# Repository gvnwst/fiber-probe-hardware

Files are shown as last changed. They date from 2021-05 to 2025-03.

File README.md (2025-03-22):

# Hardware designs for fiber probing

This is a collection of designs I started creating during my graduate career at MIT. 
I was frustrated by the poor selection of both commercial and custom options for the mounting fiber optics in a manner suitable for probing photonic integrated circuits -- particularly in the case of vertical grating couplers. 
In the history of my lab (at the least, what fraction I am aware of) there were at least four different custom approaches.
The motivations for each varied: simplicity/ease of machining, variability in fiber angle, ability to hold fiber in an intermediate clamp, and so on.

Anyway, these are my version(s). 

## Project structure
In its first iteration, there are just one or two variations of fiber holders, and one type of die mounting chuck. 
Most of my designs are made in solidworks 2018 (as time has gone on, a lot of these are Solidworks 2024), so you'll need to be able to open or convert these files to another format if you want to modify anything. 
Other filetypes (`.stl`, etc) may be made available if there is interest.

Each version of a design should be housed in its own directory and include: 
1. 3D models of all required custom parts, suitable for being sent to rapid prototyping services (`plethora`, `xometry`, and `protolabs` to name three I've used)
    1. If the new design is an update of only _part_ of a previous design, the un-changed 3D models should not be replicated. However, there should exist clear references in...
3. A bill of materials, including non-custom parts (fittings, needles, etc)
4. A document with a brief description of the design and its intended use case. This may be in the same file as the BOM. 
5. A subdirectory, often called `auxiliary files`, that stores *extra* CAD files which may be useful (e.g.  assemblies, `.stl` files for prototyping on a 3D printer). These are not designs that need to be sent out for manufacture.

## A note on license and derivative works
A creative commons license was chosen for this repository, and you the reader are encouraged to use and upgrade these designs! 
I would additionally ask that if you think up a genius improvement, or are inspired to create something better, that you also share those designs publically. 
You can do that here, by making a pull request, or through your own project -- I'm happy to reference other projects in this documentation. 
Anything to avoid some other poor grad student from going through the process, again.

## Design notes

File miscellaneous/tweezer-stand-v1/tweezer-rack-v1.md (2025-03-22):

# Tweezer Rack Version 1

This design is a rack which holds tweezers, particularly the types and sizes used to manipulate small chips up to 150 mm wafers. 
It is intended to be rigidly affixed to a table or surface via the pair of holes on the bottom flange (or adhesive tape, if no appropriate surface for threading into/drilling through is available). 
Flush-head studs are screwed into the threaded holes from the back side of the main flange. 
Tweezers are hung off this, akin to a coat rack. 
Alternately, tweezers may be inserted into the top rectangular slots, handle-first. 
The round holes on each side hold many standard size pens or sharpies.

It is stable with tweezers hung on the primary surface, but may be tippy if only the top slots are loaded.

The design is a replica of the tweezer stands used in MIT's cleanroom facilities (MIT Nano), the designs for which were kindly provided by Jorg Scholvin.
Jorg had these manufactured at [send-cut-send](https://sendcutsend.com/). They provide anodized finishes and can mount flush studs (0.5 inch) into the threaded holes.

A ready-to-manufacture `DXF` of the flattened part is included in the design directory. 

## Bill of Materials

| Description  | Vendor/Manufacturer | Part Number | Quantity | Comments |
| ------------- | ------------- | ------------- | ------------- | ---- |
| Tweezer Rack 	|	Custom	|	tweezer-rack-v1	| 	1	| 	 	|

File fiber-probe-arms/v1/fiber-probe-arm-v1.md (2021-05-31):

# fiber probe arm v1: Angle-adjustable mounting with rigid needle guides

This design is an arm for holding fiber optics with an adjustable angle (15 deg. nominal), with flexibility for using PM fiber (some in-place rotational adjustability).

The fiber itself is held in steel Luer-lock needles whose inside diameter is slightly larger than that of a fiber with its polymer coating intact.
These needles are clamped into a block which has a guide slot machined into it, and the block is mounted on a flange which pivots around a screw.
Another screw provides a few degrees of adjustability in the fiber angle, with small springs providing the counter-action to the adjustment screw.
With the pivot point at the end of the arm, this is much more convenient than using a goniometer to mount a fixed arm, but it's still not gimbaled around the fiber tip.

### Comments on assembly
The fiber may be affixed in the needles a few ways. Most obvious is simply potting with epoxy/glue, for cleaved-facet fibers (which frequently contact the die) the inability to re-cleave can be a problem.
Alternatively, I have been using the last item in the BOM to sort of strain-relieve the fiber into the Luer-lock end of the needle.
I cut a ~1 cm long section of the rubber rod and use a razor blade to make a slice along its length, slightly deeper than the center of the rod.
This should look a bit like a hot dog bun -- and the fiber rests inside the piece much like a hot dog in its bun!
The high friction coefficient of the rubber provides a good hold on the fiber, and the rubber can be jammed into the Luer needle's end.

You may find it helpful to buy a slightly over-sized rubber rod and taper the end which will be stuck into the needle.
I create a "taper" by just making a single angled cut from ~the center of the needle end to the outside of the rod about 50% of the way along its length.
See the file `rubber_stopper_example.SLDPRT` for a (non-scaled) representation of this.

To get the balance of screw tightness and spring restoring force right, I actually use two springs -- one mounted into each dowel pin slot.
You could just find stronger springs.

## Bill of Materials

| Description  | Vendor/Manufacturer | Part Number | Quantity | Comments |
| ------------- | ------------- | ------------- | ------------- | ---- |
| Arm cantilever 	|	Custom	|	 fiber-arm-cantilever-v1		| 	1	| 	 	|
| Mounting block	|	Custom 	| 	fiber-mount-block-v1	|	1	|	 |
| Block flange 	|	Custom 	| 	fiber-flange-v1	|	1	|	Should be sheet metal fabbed from stainless steel sheet |
| Clamping plate	|	Custom 	| 	fiber-clamp-plate-v1	|	1	|	 |
| Dowel pins | McMaster | 	97395A403	|	1	| Can use 2	|
| Springs 	 | McMaster | 9432K210		|	1	|  Can use 2	|
| 2-56 screws, 1/8" 	 | McMaster | 	92196A074	|	4	| Mount block to flange, clamp plate to block  |
| 2-56 screws, 1/4" 	 | McMaster | 	92196A077	|	1	| Mount flange to arm cantilever |
| 2-56 screws, 1/2" 	 | McMaster | 	92196A081	|	1	| Adjustment screw for tilt  |
| 2-56 lock washers 	 | McMaster | 92147A410		|	1	|  |
| Luer-lock needles 	 | McMaster | 6710A31		|	1	| 23 gauge |
| Rubber rod 	 | McMaster | 		|	1	| Diameter?? |

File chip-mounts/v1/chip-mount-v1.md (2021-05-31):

# chip mount v1: a low-upward-expansion TEC vacuum chuck for small to medium die

This design is a vacuum chip mount with thermal control through a TEC.
It is designed to minimize thermal expansion-induced vertical displacement in chip position -- critical for stable fiber-die position during thermal sweeps.
The expansion is minimized in two ways: the chuck on which the die sits is supported by a top-mounted flange, such that the expansion happens _downward_, and the flange itself is made from low-thermal-expansion steel.
In order to support vacuum lines/the bulky NPT-threaded hose nipple, the chuck is somewhat thick.
For this reason, I have them machined from high thermal conductivity copper.
Wiring from the thermistor and TEC to your TEC driver are left up to you.

The provided flange design is set up to mount to a Newport Ultralign 561D-YZ stage, but it mounts to anything with 1" separated #8 screws.

A glaring omission from the BOM below is a heatsink to mount on the TEC's hot side.
I haven't been able to find a good quality copper/aluminum heatsink in the correct form factor -- for my probe stations, I'm using a large skived copper heatsink (scrounged from the lab) which I cut to the correct size using a bandsaw (the rough edges can be cleaned up with a dremel).

Another heatsink option would be water cooling, if your lab has extra chillers around.
A block for liquid cooling the TEC would be pretty easy to design.
I have avoided it so far due to concerns about vibration of the heatsink, but I have never quantitatively tested these concerns.

## Bill of Materials

| Description  | Vendor/Manufacturer | Part Number | Quantity | Comments |
| ------------- | ------------- | ------------- | ------------- | ---- |
| Chip mount 	|	Custom	|	 mount-chuck-v1		| 	1	| 	Copper 	|
| Mounting flange	|	Custom 	| 	mount-flange-v1	|	1	|	Stainless steel |
| Vacuum hose fitting | McMaster | 5463K54		|	1	|	|
| Vacuum hose 	 | McMaster | 5233K52		|	1	| 	|
| Brass screws 	 | McMaster | 5233K52		|	1	| Attach chuck to flange |
| TEC module 	|	Digikey	|	1681-1190-ND |	1	|	|
| Thermistor (10k) |	Digikey |	235-1423-ND | 1 |	|

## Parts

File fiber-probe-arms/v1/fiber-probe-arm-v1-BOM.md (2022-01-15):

# fiber probe arm v1: Angle-adjustable mounting with rigid needle guides

This design is an arm for holding fiber optics with an adjustable angle (15 deg. nominal), with flexibility for using PM fiber (some in-place rotational adjustability).

The fiber itself is held in steel Luer-lock needles whose inside diameter is slightly larger than that of a fiber with its polymer coating intact.
These needles are clamped into a block which has a guide slot machined into it, and the block is mounted on a flange which pivots around a screw.
Another screw provides a few degrees of adjustability in the fiber angle, with small springs providing the counter-action to the adjustment screw.
With the pivot point at the end of the arm, this is much more convenient than using a goniometer to mount a fixed arm, but it's still not gimbaled around the fiber tip.

### Comments on assembly
The fiber may be affixed in the needles a few ways. Most obvious is simply potting with epoxy/glue, for cleaved-facet fibers (which frequently contact the die) the inability to re-cleave can be a problem.
Alternatively, I have used some soft rubber rod to sort of strain-relieve the fiber into the Luer-lock end of the needle.
I cut a ~1 cm long section of the rubber rod and use a razor blade to make a slice along its length, slightly deeper than the center of the rod.
This should look a bit like a hot dog bun -- and the fiber rests inside the piece much like a hot dog in its bun!
The high friction coefficient of the rubber provides a good hold on the fiber, and the rubber can be jammed into the Luer needle's end.

You may find it helpful to buy a slightly over-sized rubber rod and taper the end which will be stuck into the needle.
I create a "taper" by just making a single angled cut from ~the center of the needle end to the outside of the rod about 50% of the way along its length.
See the file `rubber_stopper_example.SLDPRT` for a (non-scaled) representation of this.

Alternatively (and what I actually do now, it's so much better) I designed some fixtures which clamp onto the end of the Luer-lock needles and magnetically hold the fiber in place (analogous to products from Thorlabs, Luminos, etc). 

To get the balance of angle adjustment screw screw tightness and spring restoring force right, I actually use two springs -- one mounted into each dowel pin slot.
You could just find stronger springs.

## Bill of Materials

| Description  | Vendor/Manufacturer | Part Number | Quantity | Comments |
| ------------- | ------------- | ------------- | ------------- | ---- |
| Arm cantilever 	|	Custom	|	 fiber-arm-cantilever-v1		| 	1	| 	 	|
| Mounting block	|	Custom 	| 	fiber-mount-block-v1	|	1	|	 |
| Block flange 	|	Custom 	| 	fiber-flange-v1	|	1	|	Should be sheet metal fabbed from stainless steel sheet |
| Clamping plate	|	Custom 	| 	fiber-clamp-plate-v1	|	1	|	 |
| Dowel pins | McMaster | 	97395A403	|	1	| Can use 2	|
| Springs 	 | McMaster | 9432K210		|	1	|  Can use 2	|
| 2-56 screws, 1/8" 	 | McMaster | 	92196A074	|	4	| Mount block to flange, clamp plate to block  |
| 2-56 screws, 1/4" 	 | McMaster | 	92196A077	|	1	| Mount flange to arm cantilever |
| 2-56 screws, 1/2" 	 | McMaster | 	92196A081	|	1	| Adjustment screw for tilt  |
| 2-56 lock washers 	 | McMaster | 92147A410		|	1	|  |
| Luer-lock needles 	 | McMaster | 6710A31		|	1	| 23 gauge |

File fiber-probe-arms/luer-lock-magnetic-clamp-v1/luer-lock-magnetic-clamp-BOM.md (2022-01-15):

# Magnetic clamping fiber holders for Luer-Lock needles

A weakness of the Luer-Lock needles is that the fibers are difficult to hold.
A trimmed rubber grommet works, but it's difficult. Inspired by the magnetic fiber clamps on our fusion splicer (and cleaver, etc, magnetic portion similar to [these](https://www.ozoptics.com/news/pr_173.html)), here's a piece of hardware which clamps onto the steel Luer lock needles and magnetically clamps your fibers into place. Easy-peasy fiber length adjustment.
It should also allow rotational adjustment for PM fiber, just loosen one of the collar screws and turn the whole chuck. More permanent clamping of the fiber may require adjustments.

The rubber sheet will need to be cut into a strip about 0.2" wide and just under 0.5" wide, then glued into the appropriately-sized slot on the clamp flange.
This will provide a friction surface to hold the fiber into the groove.

BOM is *per fiber clamp*. You'll want two (at least) for each probe station, input and output fibers.
Of course, some items have a large quantity and do not need multiples ordered when constructing more than one fiber clamp.

The base and collar are designed for ~perfect fitting around the Luer-Lock needle necks.
You may find that it's a bit loose. To solve this, simply take the collar and rub it (the face which contacts the base) against some medium-grit sandpaper until a few thousandths are taken off, so
Re-check fit, keep going if necessary -- you can take off a lot, needbe.

## Bill of Materials

| Description  | Vendor/Manufacturer | Part Number | Quantity | Comments |
| ------------- | ------------- | ------------- | ------------- | ---- |
| Base    |	Custom	|	 	clamp-base-v1	| 	1	| 	Aluminum 	|
| Flange  |	Custom 	|  clamp-flange-v1 |	1	|	Aluminum or steel  |
| Collar  |	Custom 	|  clamp-collar-v1 |	1	|	Aluminum |
| Dowel rod | McMaster | 98381A423	|	1 | Pack of 50	|
| Rare earth magnets | McMaster | 5862K101	|	3 | 	|
| Contact adjustment screw | McMaster | 92765A005	|	1 | 4-40 x 3/16" setscrew, alloy steel	|
| Rubber rod | McMaster | 1775T21	|	1 |  Foot, 40A durometer (medium soft)	|

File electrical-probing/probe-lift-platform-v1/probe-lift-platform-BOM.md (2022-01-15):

# lever-lifted electrical probe mount v1: A small, cheap version of the platform lifting you get on real probe stations

## Bill of Materials

| Description  | Vendor/Manufacturer | Part Number | Quantity | Comments |
| ------------- | ------------- | ------------- | ------------- | ---- |
| Cam 	         |	Custom	|	 cam-v1		| 	2	| 	Steel recommended 	|
| Front spindle  |	Custom 	|  spindle-v1 |	1	|	 |
| Rear spindle	 |	Custom 	|  rear_spindle-v1 |	2	|	Frontward for chassis rigidity |
| Chassis leg	   |	Custom 	|  chassis_side-v1 |	1	|	 |
| Top surface	   |	Custom 	|  top_plate-v1    |	1	|	Steel or other magnetic |
| Top surface	   |	Custom 	|  top_plate-v1    |	1	|	Steel or other magnetic |
| PTFE spindle bearing for front  | McMaster | 2706T17		|	2 |	|
| PTFE spindle bearing for rear   | McMaster | 2706T13		|	2 |	|
| Bearing housing for rear        | McMaster | 3971N17    |	2 |	|
| Dowel pins | McMaster | 	97395A403	|	1	| Shared with fiber probe arms v1	|
| 10-32 hex nut | McMaster | 	91841A195	|	1	| Box of 100. Lock height adjustment	|
| 10-32 carriage bolt | McMaster | 	92356A257	|	1	| Box of 50. Set height adjustment	|
| #4-40 bolts | McMaster | 	92196A109	|	1	| Attach lever arm to cam. 7/16". 3/8" or 1/2" should also work |
| #4-40 lock washer | McMaster | 	92147A415	|	1	| Attach lever arm to cam. |
| Lever arm grip | McMaster | 	9282K83	|	1	| Set of six	|
| Lever arm rest | McMaster | 	92196A546	|	1	| Box of 25. Partially-threaded machine screw. Also need nut. 	|
| Lever arm rest adjustment | McMaster | 	94355A700	|	1	| 4-40 setscrew. Also need nut. |

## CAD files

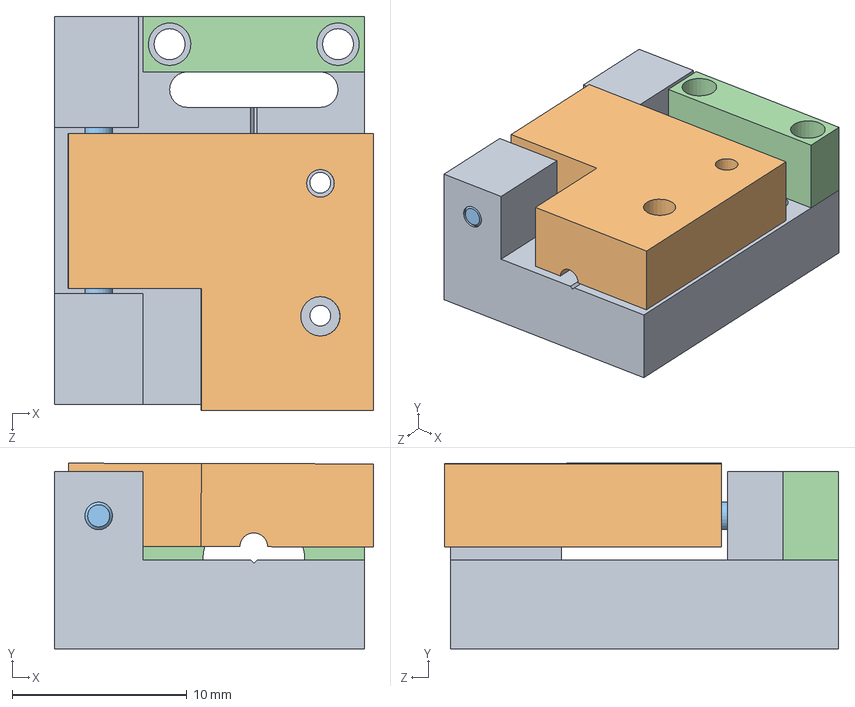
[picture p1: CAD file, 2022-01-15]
fiber-probe-arms/luer-lock-magnetic-clamp-v1/auxiliary files/Magnetic fiber clamp assembly v1.SLDASM
18.3 x 10.6 x 22.6 mm
clamp-base-v1
clamp-flange-v1
98381A423_ALLOY STEEL DOWEL PIN
clamp-collar-v1

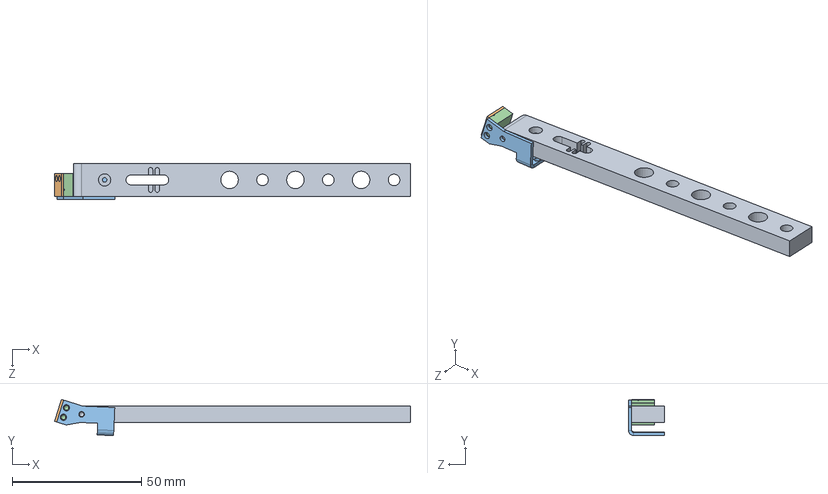
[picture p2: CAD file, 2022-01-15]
fiber-probe-arms/v1/fiber-assembly-v1.SLDASM
137.5 x 14.0 x 13.9 mm
fiber-arm-cantilever-v1
fiber-clamp-plate-v1
fiber-flange-v1
fiber-mount-block-v1

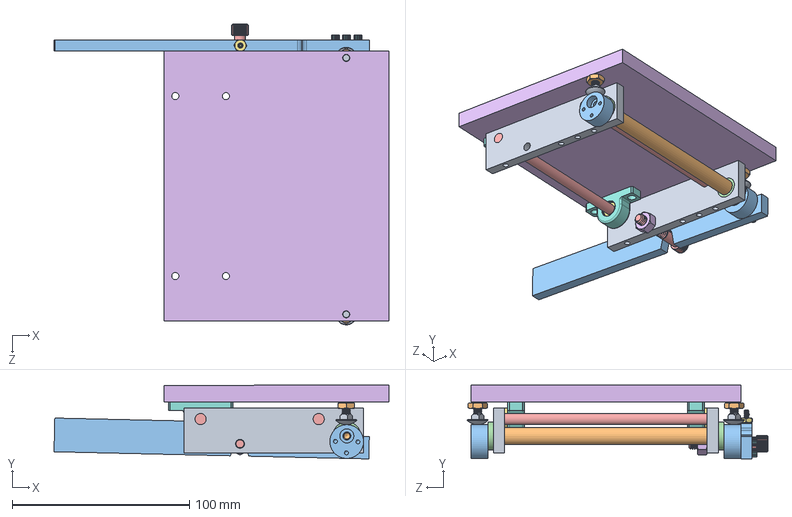
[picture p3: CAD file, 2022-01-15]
electrical-probing/probe-lift-platform-v1/auxiliary-cad/probe-lift-platform-assembly.SLDASM
189.1 x 41.7 x 169.8 mm
chassis_side-v1 x 2
front_spindle-v1
cam-v1 x 2
ptfe-spindle x 2
rear_spindle-v1 x 2
top_plate-v1
ptfe-spindle-rear x 2
bearing-housing x 2
10-32-0625_carriage_bolt x 2
10-32 hex nut x 2
lever-arm-v1
4-40 setscrew
14-20 bolt
14-20 nut
4-40 nut
4-40 7-16in screw x 3

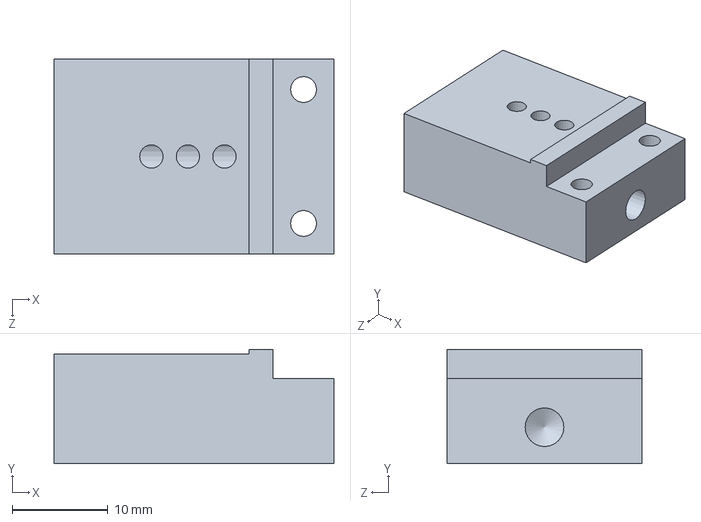
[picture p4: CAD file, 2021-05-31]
chip-mounts/v1/mount-chuck-v1.SLDPRT
29.2 x 11.9 x 20.3 mm

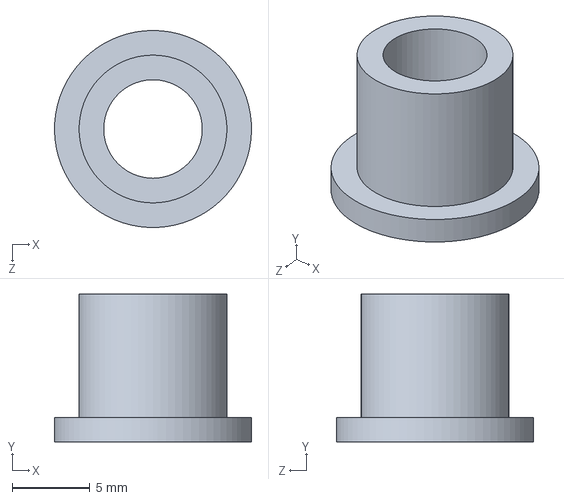
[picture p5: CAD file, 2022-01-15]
electrical-probing/probe-lift-platform-v1/auxiliary-cad/ptfe-spindle-rear.SLDPRT
12.7 x 9.53 x 12.7 mm

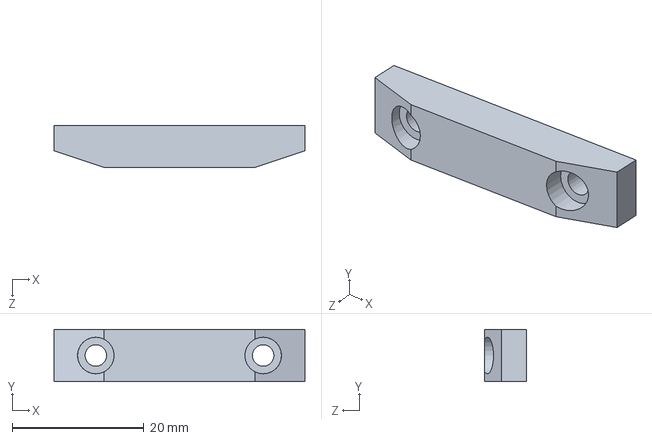
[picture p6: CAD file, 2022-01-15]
electrical-probing/probe-lift-platform-v1/cam_runner-v1.SLDPRT
38.1 x 7.94 x 6.35 mm

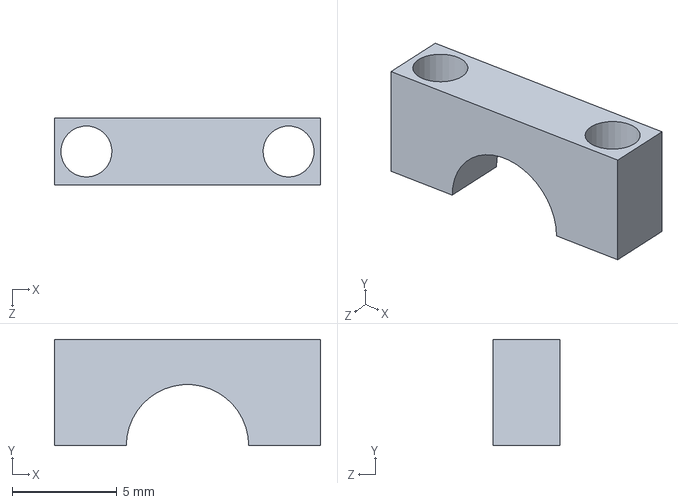
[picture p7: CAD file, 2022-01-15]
fiber-probe-arms/luer-lock-magnetic-clamp-v1/clamp-collar-v1.SLDPRT
12.7 x 5.08 x 3.17 mm

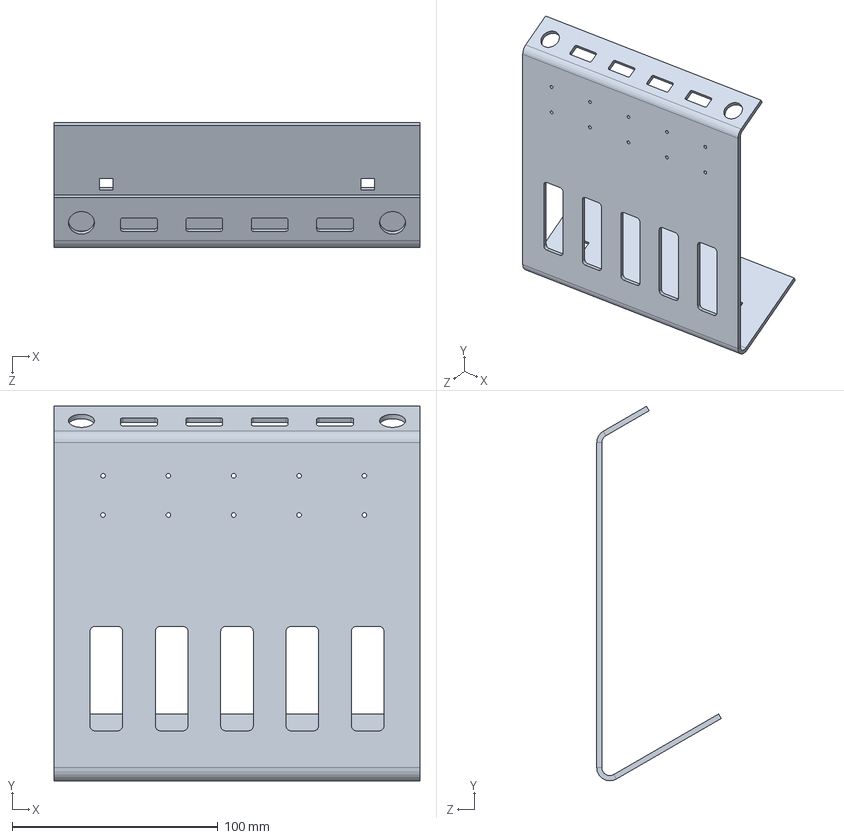
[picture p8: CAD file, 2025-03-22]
miscellaneous/tweezer-stand-v1/tweezer-rack-v1.SLDPRT
177.8 x 182.0 x 60.5 mm

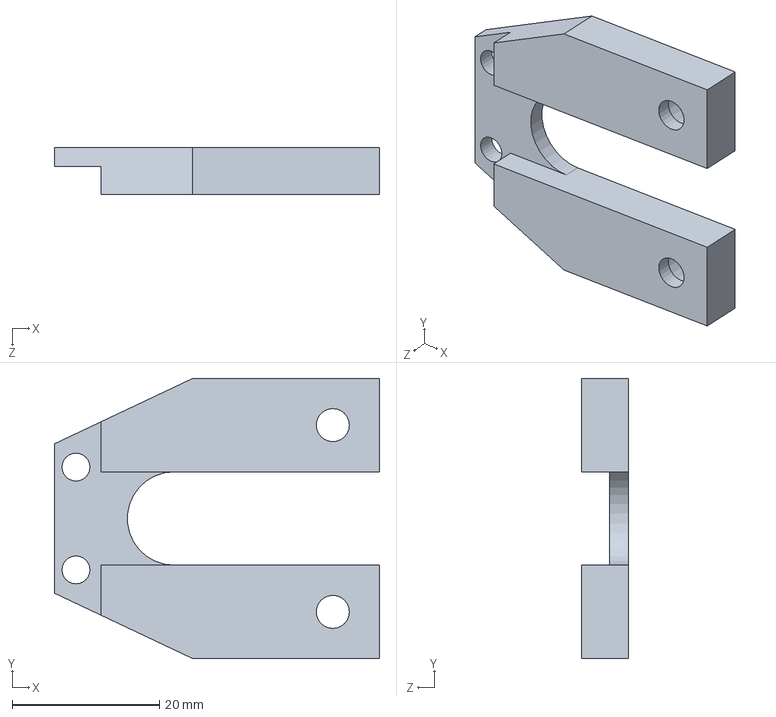
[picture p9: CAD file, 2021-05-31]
chip-mounts/v1/mount-flange-v1.SLDPRT
44.2 x 38.1 x 6.35 mm

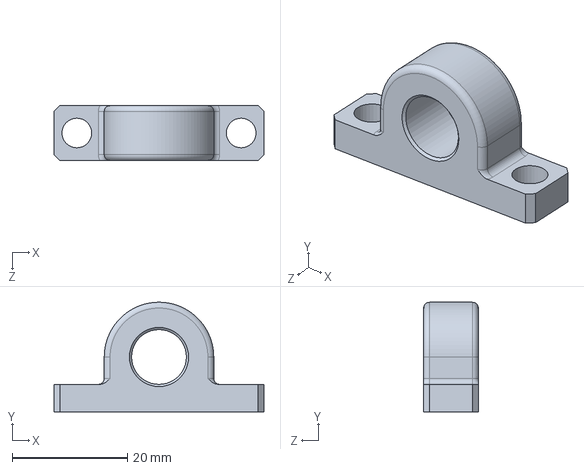
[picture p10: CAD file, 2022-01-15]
electrical-probing/probe-lift-platform-v1/auxiliary-cad/bearing-housing.SLDPRT
36.5 x 19.0 x 9.53 mm

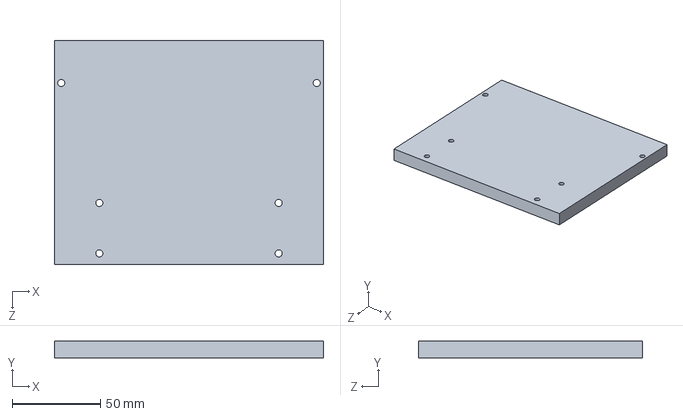
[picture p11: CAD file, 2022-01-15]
electrical-probing/probe-lift-platform-v1/top_plate-v1.SLDPRT
152.4 x 9.53 x 127.0 mm

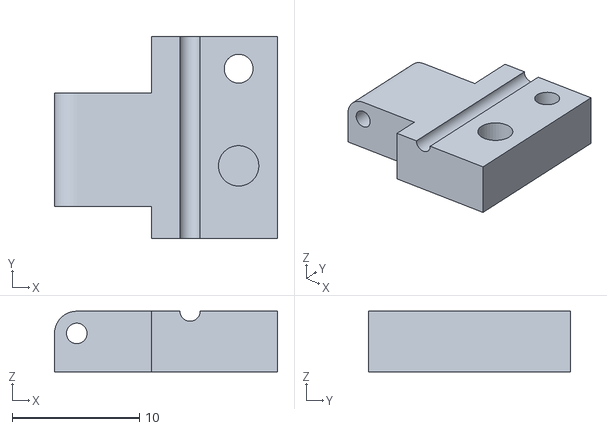
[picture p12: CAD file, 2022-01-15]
fiber-probe-arms/luer-lock-magnetic-clamp-v1/auxiliary files/clamp-flange-v1.STL
17.5 x 15.9 x 4.76

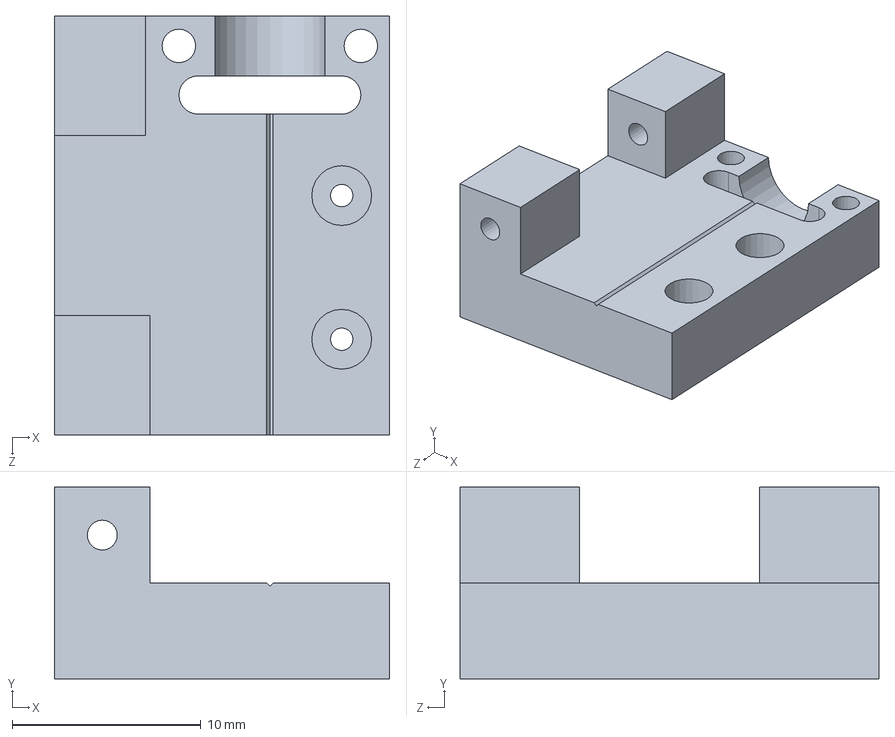
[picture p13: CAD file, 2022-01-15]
fiber-probe-arms/luer-lock-magnetic-clamp-v1/clamp-base-v1.SLDPRT
17.8 x 10.2 x 22.2 mm

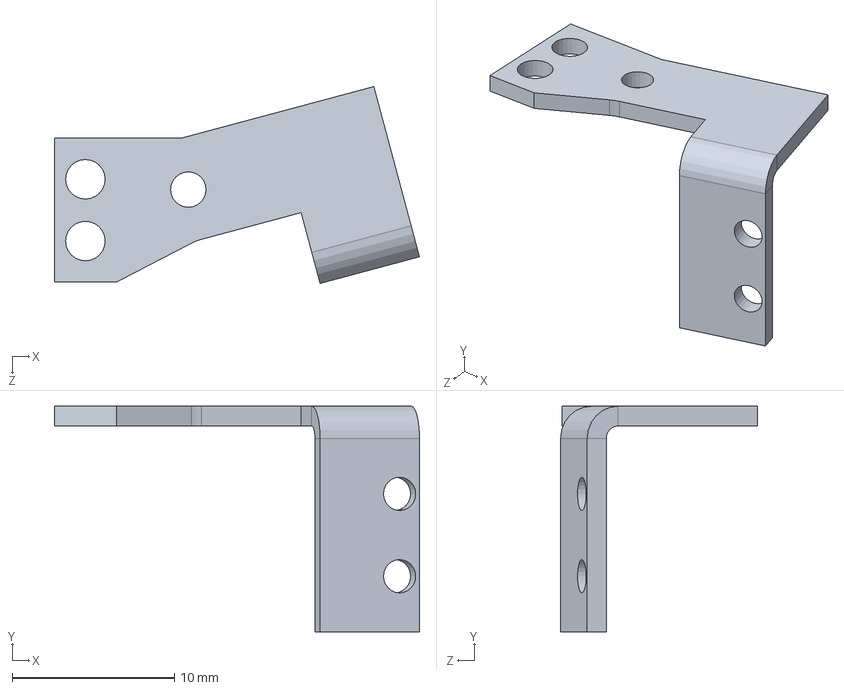
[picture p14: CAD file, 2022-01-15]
fiber-probe-arms/v1/fiber-flange-v1.SLDPRT
22.5 x 13.9 x 12.1 mm

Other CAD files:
miscellaneous/tweezer-stand-v1/tweezer-rack-v1-FlatPattern.DXF
electrical-probing/probe-lift-platform-v1/front_spindle-v1.SLDPRT
fiber-probe-arms/luer-lock-magnetic-clamp-v1/clamp-flange-v1.SLDPRT
fiber-probe-arms/v1/fiber-arm-cantilever-v1.SLDPRT
electrical-probing/probe-lift-platform-v1/auxiliary-cad/10-32 hex nut.SLDPRT
electrical-probing/probe-lift-platform-v1/auxiliary-cad/10-32-0625_carriage_bolt.SLDPRT
electrical-probing/probe-lift-platform-v1/auxiliary-cad/14-20 bolt.SLDPRT
electrical-probing/probe-lift-platform-v1/auxiliary-cad/14-20 nut.SLDPRT
electrical-probing/probe-lift-platform-v1/auxiliary-cad/4-40 7-16in screw.SLDPRT
electrical-probing/probe-lift-platform-v1/auxiliary-cad/4-40 lock washer.SLDPRT
electrical-probing/probe-lift-platform-v1/auxiliary-cad/4-40 nut.SLDPRT
electrical-probing/probe-lift-platform-v1/auxiliary-cad/4-40 setscrew.SLDPRT
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

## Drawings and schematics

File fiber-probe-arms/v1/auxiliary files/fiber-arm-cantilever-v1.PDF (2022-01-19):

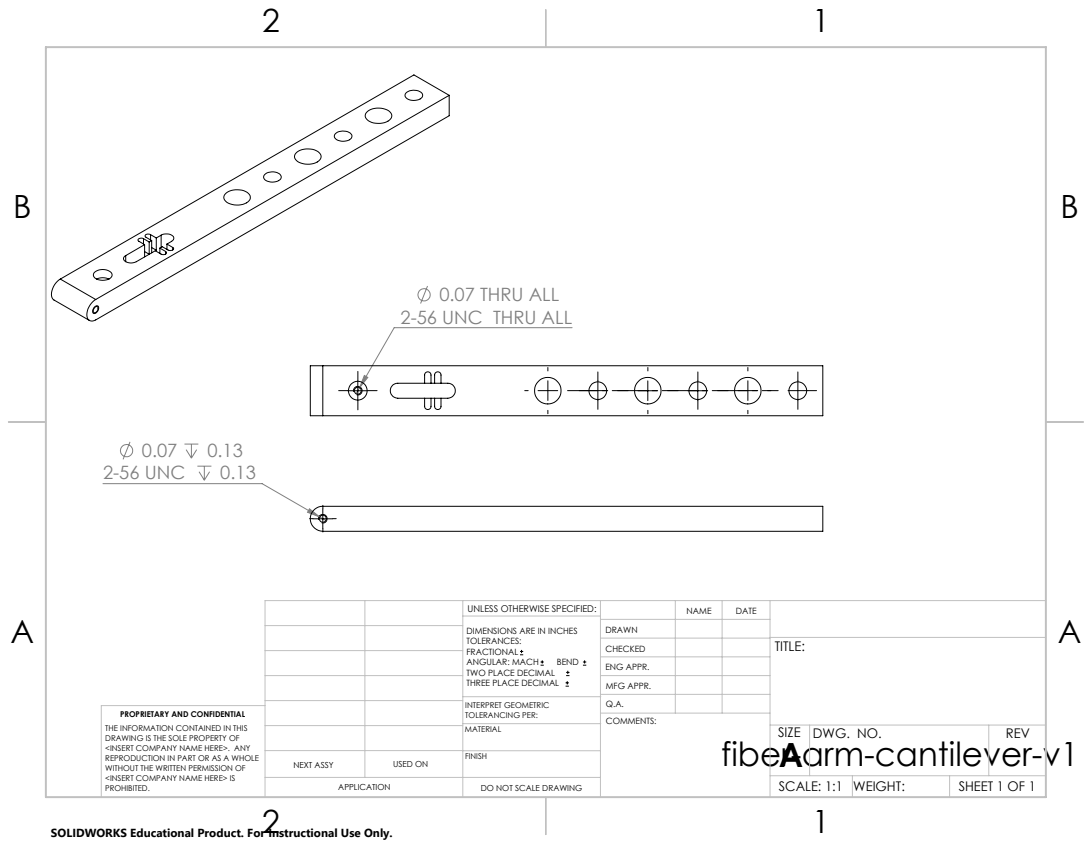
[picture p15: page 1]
2-56 UNC

0.07 THRU ALL
2-56 UNC THRU ALL

UNLESS OTHERWISE SPECIFIED: | | NAME | DATE
DIMENSIONS ARE IN INCHES TOLERANCES: FRACTIONAL ANGULAR: MACH BEND TWO PLACE DECIMAL THREE PLACE DECIMAL | DRAWN

CHECKED | | | TITLE:

ENG APPR.
MFG APPR.

INTERPRET GEOMETRIC TOLERANCING PER: | Q.A.
MATERIAL | | SIZE A | DWG. NO. | REV

PROPRIETARY AND CONFIDENTIAL
THE INFORMATION CONTAINED IN THIS
DRAWING IS THE SOLE PROPERTY OF
<INSERT COMPANY NAME HERE>. ANY
REPRODUCTION IN PART OR AS A WHOLE
WITHOUT THE WRITTEN PERMISSION OF
<INSERT COMPANY NAME HERE> IS
PROHIBITED.

NEXT ASSY | USED ON | FINISH

APPLICATION | DO NOT SCALE DRAWING | | SCALE: 1:1 | WEIGHT: | SHEET 1 OF 1

SOLIDWORKS Educational Product. For Instructional Use Only.

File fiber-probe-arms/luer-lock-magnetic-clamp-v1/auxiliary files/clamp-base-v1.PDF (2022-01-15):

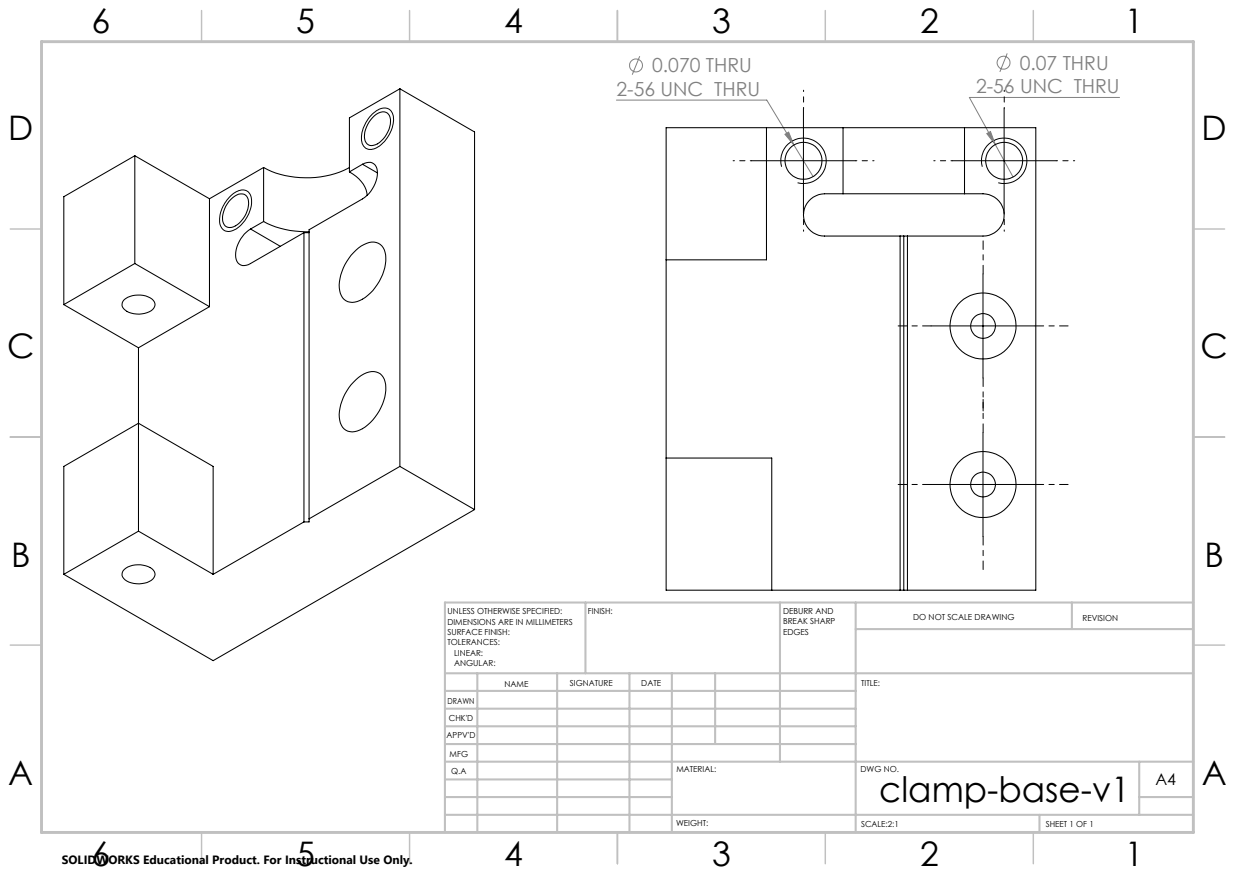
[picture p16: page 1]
0.070 THRU 2-56 UNC THRU; 0.07 THRU 2-56 UNC THRU; FINISH:; DEBURR AND; BREAK SHARP; DO NOT SCALE DRAWING; REVISION; SCALE:2:1; SHEET 1 OF 1

UNLESS OTHERWISE SPECIFIED:
DIMENSIONS ARE IN MILLIMETERS
SURFACE FINISH:
TOLERANCES:
LINEAR:
ANGULAR:

NAME | SIGNATURE | DATE | | | | TITLE:

DRAWN
CHK'D
APPV'D
MFG
Q.A | | | | MATERIAL: | DWG NO. clamp-base-v1 | A4

SOLIDWORKS Educational Product. For Instructional Use Only.

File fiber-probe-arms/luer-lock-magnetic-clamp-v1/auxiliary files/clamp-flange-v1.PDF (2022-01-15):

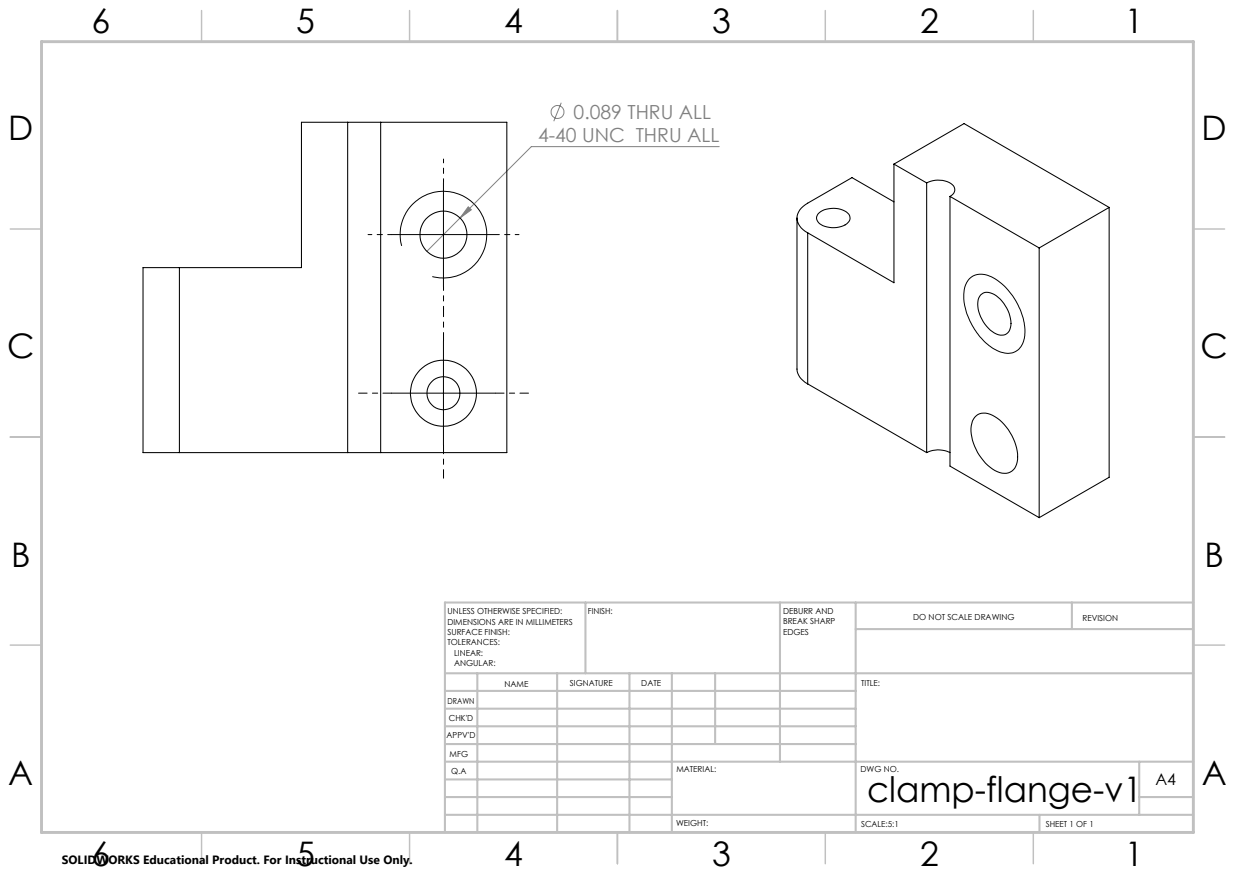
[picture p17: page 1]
FINISH:; DEBURR AND; BREAK SHARP; DO NOT SCALE DRAWING; REVISION; SCALE:5:1; SHEET 1 OF 1

0.089 THRU ALL
4-40 UNC THRU ALL

UNLESS OTHERWISE SPECIFIED:
DIMENSIONS ARE IN MILLIMETERS
SURFACE FINISH:
TOLERANCES:
LINEAR:
ANGULAR:

NAME | SIGNATURE | DATE | | | | TITLE:

DRAWN
CHK'D
APPV'D
MFG
Q.A | | | | MATERIAL: | DWG NO. clamp-flange-v1 | A4

SOLIDWORKS Educational Product. For Instructional Use Only.

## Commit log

2021-05-31 Adding chip mount v1
    [mount-chuck-v1.SLDPRT, mount-flange-v1.SLDPRT]
2021-05-31 Adding fiber probe arm v1
    [fiber-arm-cantilever-v1.SLDPRT, fiber-assembly-v1.SLDASM, fiber-clamp-plate-v1.SLDPRT, fiber-flange-v1.SLDPRT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]
2022-01-15 Creating a kinematic platform for fast adjustment of RF probes
    [10-32 hex nut.SLDPRT, 10-32-0625_carriage_bolt.SLDPRT, 14-20 bolt.SLDPRT, 14-20 nut.SLDPRT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]
2022-01-15 Magnetic-clamping fiber collar for use with luer-lock needles
    [98381A423_ALLOY STEEL DOWEL PIN.SLDPRT, Magnetic fiber clamp assembly v1.SLDASM, clamp-base-v1.SLDDRW, clamp-base-v1.SLDPRT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]
2022-01-15 Small edits to fiber probe model
    [fiber-assembly-v1.SLDASM, fiber-flange-v1.SLDPRT]
2022-01-19 Generating PDFs with hole callouts for fiber probe holder v1
    [fiber-arm-cantilever-v1.SLDDRW, fiber-mount-block-v1.SLDDRW]
2025-03-22 Adding tweezer rack designs
    [tweezer-rack-v1-FlatPattern.DXF, tweezer-rack-v1.SLDPRT]
